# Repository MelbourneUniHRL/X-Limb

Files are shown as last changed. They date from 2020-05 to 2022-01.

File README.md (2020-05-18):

# X-Limb: A Practical 3D-Printed Soft Robotic Prosthetic Hand

Currently, the gap between the existing soft robotic hand designs and the practical requirements significantly hampers the potential to transfer 
these designs to real-world applications. These requirements are:
- Light weight (less than the average weight of a human hand) 
- Intrinsic actuation system (embedded in the hand structure) 
- Robust finger kinematic design and compliance in the mechanical design 
- Powered thumb for multiple grasping types 
- Ease of manufacture and personalisation 
- Sufficient functionalities and the balance between the functionalities and complexity 

The X-Limb hand prosthesis design addressed these requirements with the consideration of the trade-off between practicality and performance.

**More details in the following open-access paper in PLoS ONE:**

[ Mohammadi A, Lavranos J, Zhou H, Mutlu R, Alici G, Tan Y, et al. (2020) A practical 3D-printed soft robotic prosthetic hand with multi-articulating capabilities. PLoS ONE 15(5): e0232766. https://doi.org/10.1371/journal.pone.0232766](https://journals.plos.org/plosone/article?id=10.1371/journal.pone.0232766).

**Performance of the X-Limb in carrying out activities of daily living is available in the following video in YouTube:**

[X-Limb - A Lightweight Soft Robotic Prosthetic Hand](https://youtu.be/qoeMaFlB5xs)

## Main characteristics of the X-Limb design:
**- Overall weight:** 253gr

**- Grasp types:** Three grasps types (power, pinch, and tripod) with capability of individual finger movement

**- Grip force:** Power grasp force of 21.5N and pinch grasp force of 10.2N

**- Hand closing/opening speed:** 1.3sec

**- Cost:** Bill of material cost of 200 USD (excluding quick disconnect wrist but without factoring in the cost reduction through mass production).

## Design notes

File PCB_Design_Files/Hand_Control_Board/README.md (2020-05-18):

## Hand main control board PCB design files

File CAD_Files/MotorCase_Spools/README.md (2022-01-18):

# DC motor cases and spools of different fingers
All these CAD files should be 3D printed with PLA/ABS with 100% infill.

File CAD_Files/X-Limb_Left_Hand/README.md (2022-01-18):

## STL files of the X-Limb left hand
This CAD files should be 3D printed with TPU or TPE flexible filaments. The fingers should be 3D printed in upright position without any support materials.

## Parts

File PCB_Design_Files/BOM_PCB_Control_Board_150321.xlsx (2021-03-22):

# | Designator | Description* | Footprint* | Manufacturer* | Manufacturer Part Number | Supplier | Quantity* | Accept substitution
1 | C1, C2 | 1uf 6.3V | C0603 |  | 0603F105M250NT |  | 2
2 | C5, C7, C8, C9, C10, C11, C12, C13, C14, C15, C16, C17, C18, C19, C20, C27, C28, C29 | 100nF 50V | C0603 |  | 0603F104M500NT |  | 18
3 | CP1, CP2, CP3, CP4, CP5, CP6, CP7 | 47uF 10V | CAPPM5042X550N |  | HV470M010C055R |  | 7
4 | C21, C22, C23, C30, C31, C32 | 33nF 50V | C0603 |  | GRM188R71H333KA61D |  | 6
5 | C24, C25, C26, C33, C34, C35 | 0.47uF 16V | C0603 |  | CL10B474KA8NNNC |  | 6
6 | C4, C6 | 10uF 6.3V | C0603 |  | 0603X106M6R3NT |  | 2
7 | R3, R4, R5, R6, R7, R8, R9, R10, R11, R12, R13, R16, R17, R18, R19, R20, R27, R28, R29, R39, R40, R41, R51, R52 | 1k | 0603 |  | RC0603JR-071KL |  | 26
8 | R2, R14, R15, R21, R22, R23, R24, R25, R26, R33, R34, R35, R36, R37, R38 | 100K | 0603 |  | RC0603JR-07100KL |  | 4
9 | R30, R31, R32, R42, R43, R44 | 220 | 0603 |  | RC0603JR-07220RL |  | 2
10 | R1, R45, R46, R47, R48, R49, R50 | 10k | 0603 |  | RC0603JR-0710KL |  | 7
11 | LED1, LED2, LED3 | LED RED | 0805 |  | 17-21SURC/S530-A3/TR8 |  | 1
12 | D1, D2 | B5819W-TP | SOD-123 | Micro Commercial Co | B5819W-TP (https://www.digikey.cn/en/products/detail/micro-commercial-co/B5819W-TP/3774959?WT.z_header=search_go&s=N4IgTCBcDaIEIFYAcBGAnAdQLQBUAKIAugL5A) | DigiKey | 2
13 | Q2, Q3, Q4, Q5, Q6, Q7 | 2N7002K-T1-GE3 (https://search.ickey.cn/site/index.html?keyword=2N7002K-T1-GE3) | TO-236 | Vishay Siliconix | 2N7002K-T1-GE3 (https://www.digikey.cn/en/products/detail/vishay-siliconix/2N7002K-T1-GE3/2621521?WT.z_header=search_go&s=N4IgTCBcDa4HIHYAMSwGkC0AVAjBg4gKIDMIAugL5A) | DigiKey | 6
14 | Q1 | IRF7842 | 8-SO | Infineon Technologies | IRF7842PBF-ND (https://www.digikey.cn/en/products/detail/infineon-technologies/IRF7842PBF/856673?WT.z_header=search_go&s=N4IgTCBcDaIJICUBiB2AHAFjABQEJIFoA5AERAF0BfIA) | DigiKey | 1
15 | U7, U9, U10, U16, U17, U18 | MC33926 | 32PQFN | NXP USA Inc. | MC33926PNB-ND (https://www.digikey.cn/en/products/detail/nxp-usa-inc/MC33926PNB/2185655?WT.z_header=search_go&s=N4IgTCBcDaILIGEDMSCcYBsAFAcgIQFocAREAXQF8g) | DigiKey | 6
16 | U4, U5, U6, U8, U11, U12 | SN74LVC2G08DCUT (https://search.ickey.cn/site/index.html?keyword=SN74LVC2G08DCUT) | 8VSSOP | Texas Instruments | SN74LVC2G08DCUT (https://www.digikey.cn/en/products/detail/texas-instruments/SN74LVC2G08DCUT/1592265) | DigiKey | 6
17 | U2 | ATmega2560-16AU | 100-TQFP | Microchip Technology | ATMEGA2560-16AU-ND (https://www.digikey.cn/en/products/detail/microchip-technology/ATMEGA2560-16AU/735455?WT.z_header=search_go) | DigiKey | 1
18 | U1 | NCP1117ST50T3G | SOT-223 | ON Semiconductor | NCP1117ST50T3GOSCT-ND (https://www.digikey.cn/en/products/detail/on-semiconductor/NCP1117ST50T3G/921289?WT.z_header=search_go) | DigiKey | 1
19 | Y1 | CSTCE16M0V53-R0 | 3-SMD | Murata Electronics | 490-1198-1-ND (https://www.digikey.cn/en/products/detail/murata-electronics/CSTCE16M0V53-R0/584406?WT.z_header=search_go&s=N4IgTCBcDaICwE4AMBaAjGhAOdKByAIiALoC%2BQA) | DigiKey | 1
20 | U3 | FT232RL | 28-SSOP | FTDI | 895-FT232RL (https://www.digikey.cn/en/products/detail/ftdi-future-technology-devices-international-ltd/FT232RL-REEL/1836385?WT.z_header=search_go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) | DigiKey | 1
21 | RESET | SW-PB |  | TE Connectivity | 450-1129-ND (https://www.digikey.cn/en/products/detail/te-connectivity-alcoswitch-switches/FSM4JSMA/525821?WT.z_header=search_go&s=N4IgTCBcDaICwFYAMBaAjGsBOFA5AIiALoC%2BQA) | DigiKey | 1
22 | M1, M2, M3, M4, M5, M6 | SFW5R-1STE1LF |  | Amphenol ICC (FCI) | 609-1784-1-ND (https://www.digikey.cn/en/products/detail/amphenol-icc-fci/HFW5R-1STE1LF/1002099?WT.z_header=search_go&s=N4IgTCBcDaIGwAYCcBaAjAdgBwBZ0oDkAREAXQF8g) | DigiKey | 6
23 | JC1 | MICRO USB Connector |  | Amphenol ICC (FCI) | 10118192-0001LF (https://www.digikey.cn/en/products/detail/amphenol-icc-fci/10118192-0001LF/2785387?WT.z_header=search_go&s=N4IgTCBcDaIIwAY5wBxwJxgLQN3AMgGIgC6AvkA) | DigiKey | 1

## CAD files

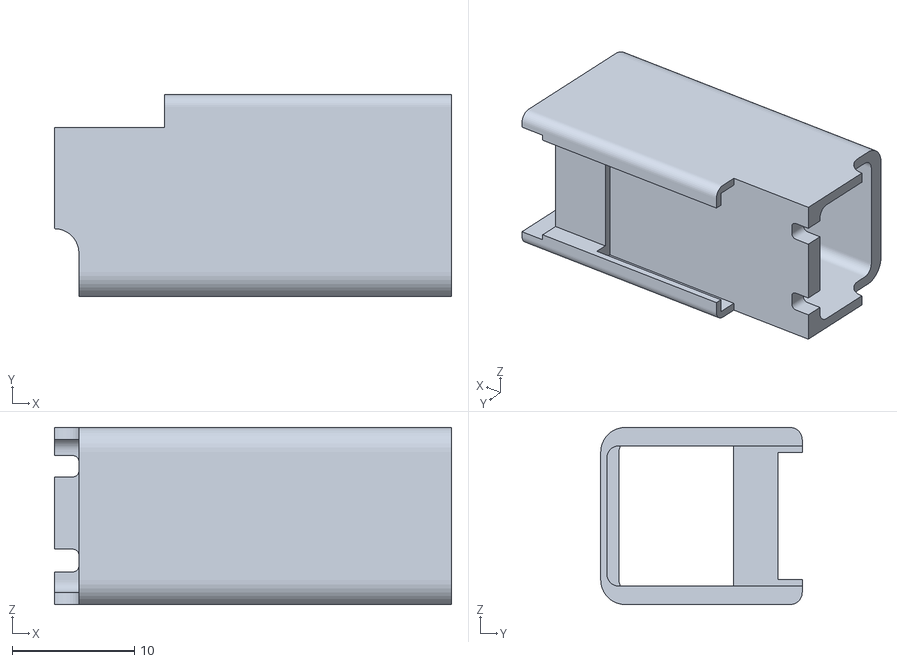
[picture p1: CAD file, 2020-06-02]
CAD_Files/MotorCase_Spools/MotorCaseBody_1000_GearRatio_Index_Middle_Thumb_Ring.STL
32.5 x 16.5 x 14.5

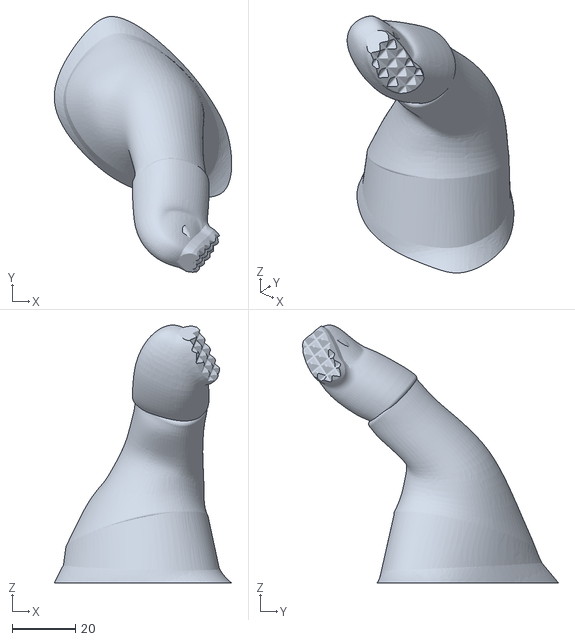
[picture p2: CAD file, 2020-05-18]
CAD_Files/X-Limb_Left_Hand/Left_Hand_Thumb.STL
56.2 x 81.0 x 81.6

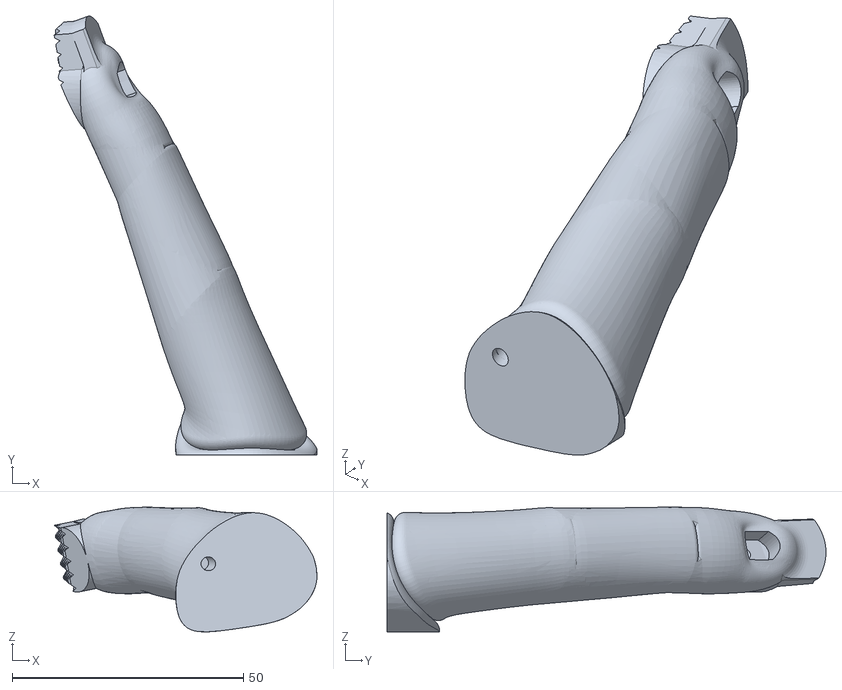
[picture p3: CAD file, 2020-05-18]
CAD_Files/X-Limb_Right_Hand/Right_Hand_Index.STL
56.9 x 94.9 x 27.0

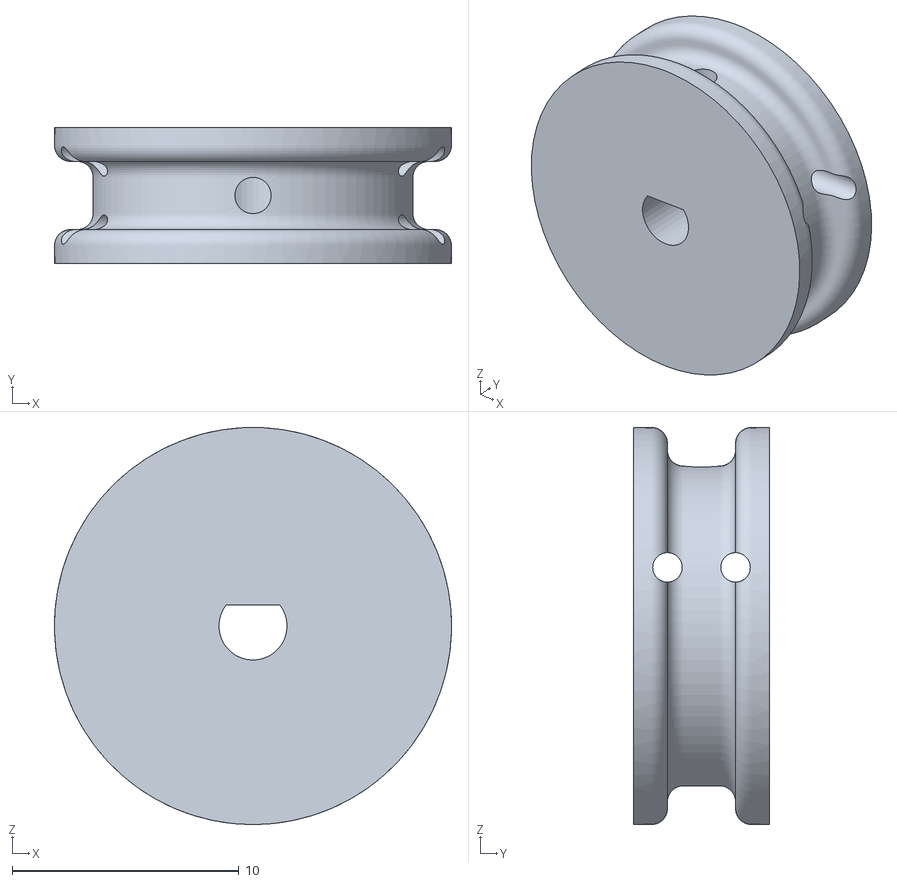
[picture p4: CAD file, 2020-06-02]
CAD_Files/MotorCase_Spools/Spool_17mm_Middle_Ring.STL
17.5 x 6.00 x 17.5

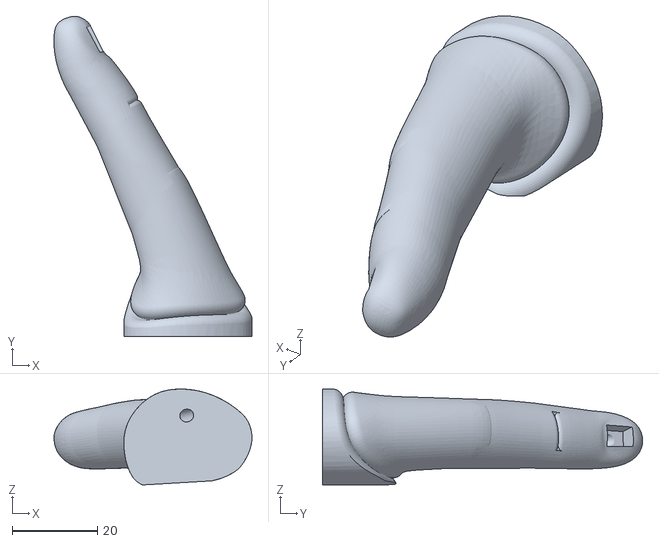
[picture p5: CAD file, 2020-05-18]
CAD_Files/X-Limb_Left_Hand/Left_Hand_Little.STL
46.4 x 75.1 x 22.5

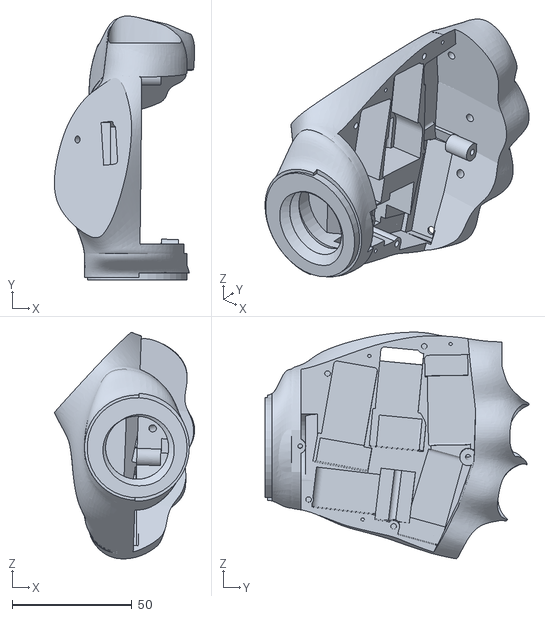
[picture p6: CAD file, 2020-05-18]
CAD_Files/X-Limb_Right_Hand/Righ_Hand_Palm.STL
58.6 x 110.3 x 94.7

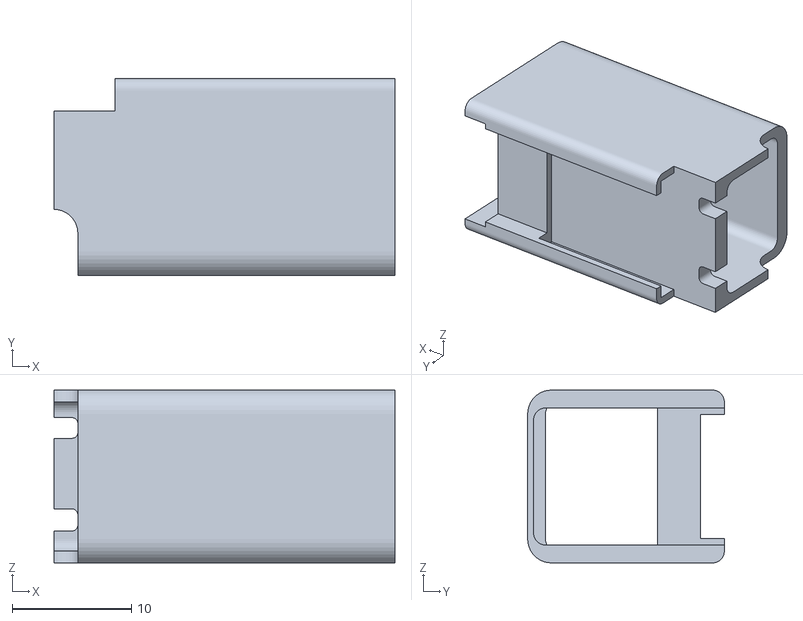
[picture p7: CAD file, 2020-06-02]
CAD_Files/MotorCase_Spools/MotorCaseBody_298_GearRatio_Little.STL
28.6 x 16.5 x 14.5

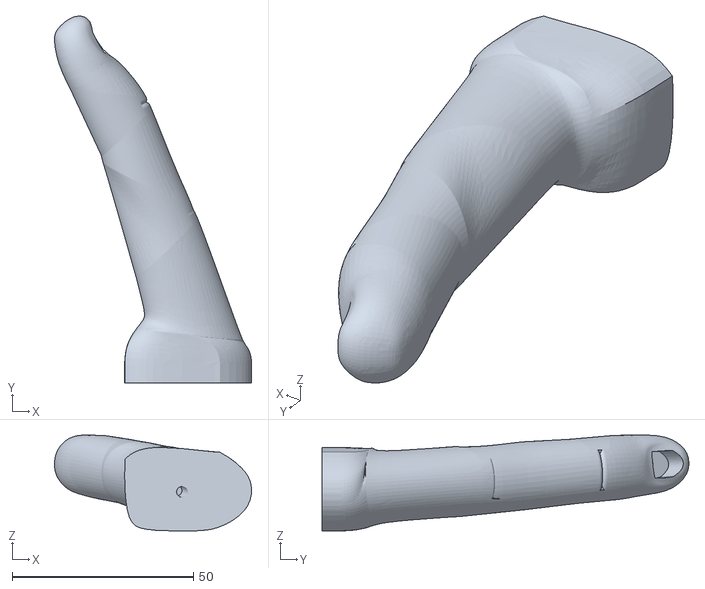
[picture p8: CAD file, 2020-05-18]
CAD_Files/X-Limb_Left_Hand/Left_Hand_Middle.STL
54.4 x 101.2 x 26.4

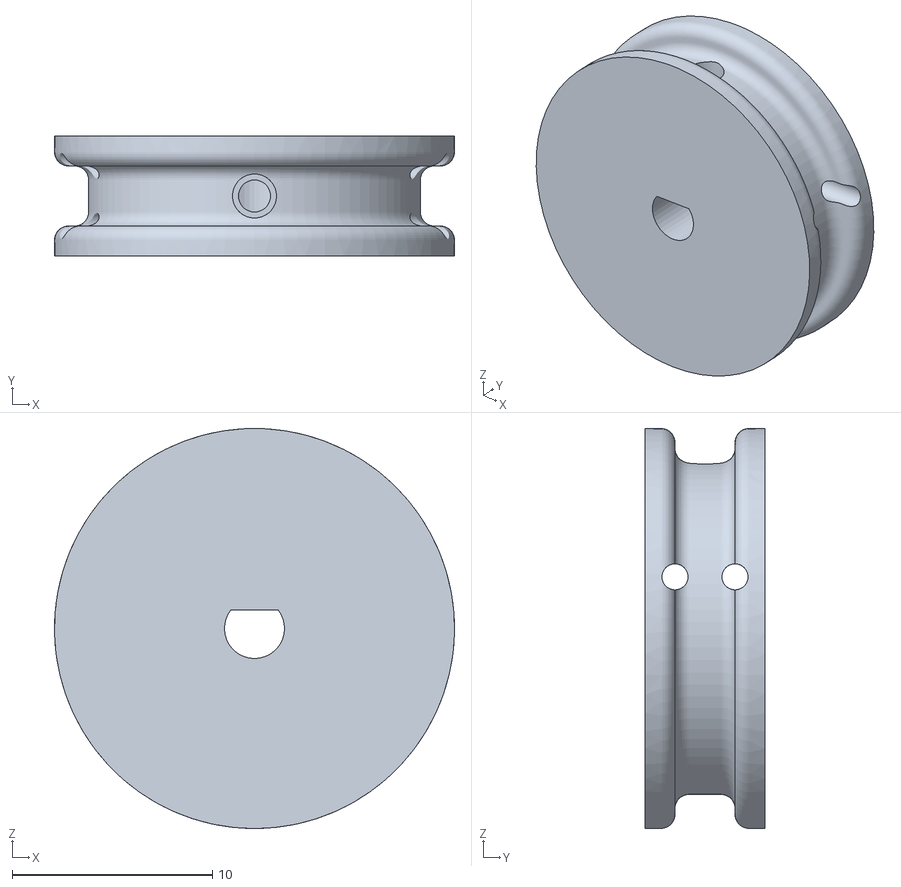
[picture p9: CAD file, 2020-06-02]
CAD_Files/MotorCase_Spools/Spool_20mm_Index_Little_Thumb.STL
20.0 x 6.00 x 20.0

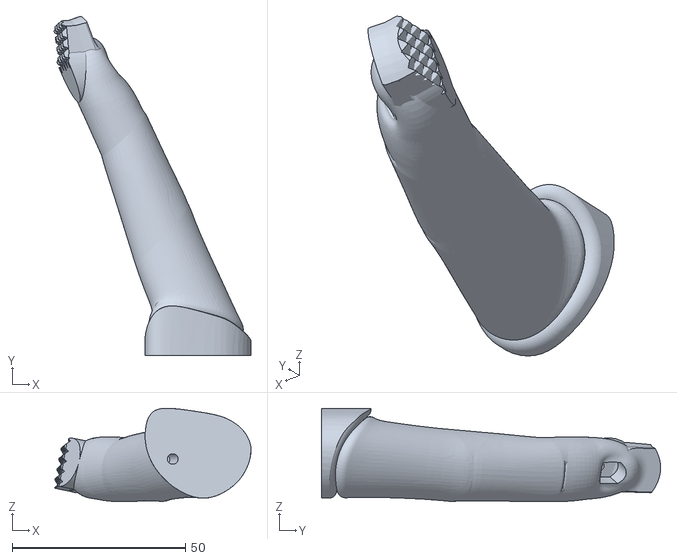
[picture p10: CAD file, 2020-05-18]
CAD_Files/X-Limb_Left_Hand/Left_Hand_Index.STL
56.9 x 97.9 x 27.0

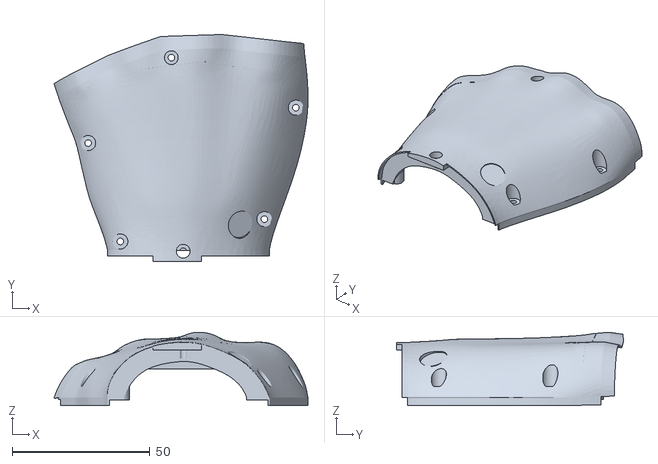
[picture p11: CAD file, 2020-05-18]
CAD_Files/X-Limb_Left_Hand/Left_Hand_Back_Cover.STL
92.1 x 82.3 x 26.6

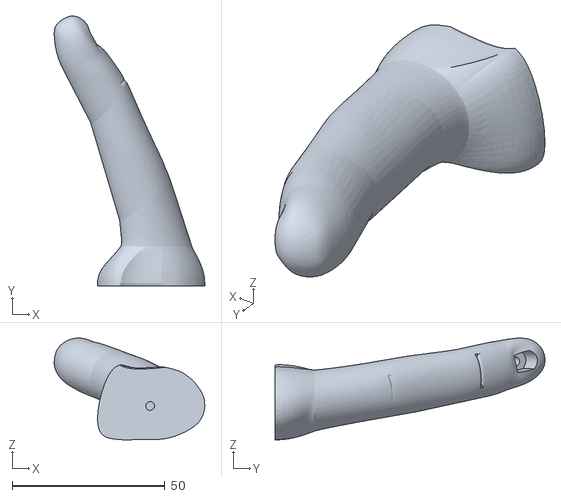
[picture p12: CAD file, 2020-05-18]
CAD_Files/X-Limb_Right_Hand/Right_Hand_Ring.STL
49.3 x 88.4 x 33.4

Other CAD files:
CAD_Files/X-Limb_Right_Hand/Right_Hand_Little.STL
CAD_Files/X-Limb_Right_Hand/Right_Hand_Thumb.STL
CAD_Files/X-Limb_Left_Hand/Left_Hand_Palm.STL
CAD_Files/X-Limb_Right_Hand/Right_Hand_Middle.STL
CAD_Files/X-Limb_Left_Hand/Left_Hand_Ring.STL
CAD_Files/X-Limb_Right_Hand/Right_Hand_Back_Cover.STL

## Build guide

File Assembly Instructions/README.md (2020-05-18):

### Instructive videos for assembly of the X-Limb components

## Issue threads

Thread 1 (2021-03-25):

### ISSUE TITLE
maybe not an issue

### ISSUE THREAD

**Issue by gasparapsag** [MelbourneUniHRL/X-Limb#1]
Hi, 

It's amazing the job that you guys have done with this, I could not find anything similar to this, just amazing! 

I'm trying to build this hand for a cousin who needs it, the thing is when I sent the boom to de PCB manufacturer they said is incomplete as they need the code of the part from mouser or Digikey. I don't know how to correctly choose some of the components as for example for capacitors besides capacitance and footprint voltage is needed to select one and resistor sometimes I can't find the correct footprint.
Here is what I have found so far.
https://drive.google.com/file/d/1TM07XncSh36at8BIBJNJwm0H0ubI7nqd/view?usp=sharing

Could you guys guide me on how to select the rest of the components?

Thank you!

**Comment by MelbourneUniHRL** [comment]
Hi,

We are glad that you found it useful. The PCBs are actually fabricated by contract manufacturer. I can ask them regarding the missing components, probably it will take a bit of time.

If you just need to make one, I have a spare controller which I can post to you at no cost.

Regards,
Alireza


------------------------------------------------------

Alireza Mohammadi
Senior Research Officer,
Department of Mechanical Engineering
The University of Melbourne, Parkville VIC 3010
Phone: +61 3 8345 4378
Email: alirezam@unimelb.edu.au
Webpage: <http://people.eng.unimelb.edu.au/doetomo/> http://people.eng.unimelb.edu.au/alirezam/

________________________________

**Comment by gasparapsag** [comment]
Hi Alireza, 

Such a great news, yes it would be nice if you can post me the controller I will pay the shipping.

Right now I want to make  just one for my cousin, she is a single mother of 4 living in precarious conditions, a few weeks ago she almost took her own life. I wasn’t aware of the psychological problems that amputees have until I got close to one. 
Now you have inspired me to help others too so I will appreciate the full list of components whenever is complete.

Thank you.
Gaspar.

**Comment by MelbourneUniHRL** [comment]
Hi Gaspar,

It is sad to hear that. Just send me your address so I can post it to you.

Her amputation is on her right hand or left hand? Is it below elbow?

I have some other spare parts that can them to you along with the controller.

Regards,
Alireza


------------------------------------------------------

Alireza Mohammadi
Senior Research Officer,
Department of Mechanical Engineering
The University of Melbourne, Parkville VIC 3010
Phone: +61 3 8345 4378
Email: alirezam@unimelb.edu.au
Webpage: <http://people.eng.unimelb.edu.au/doetomo/> http://people.eng.unimelb.edu.au/alirezam/

________________________________

**Comment by gasparapsag** [comment]
Hi Alireza, 

The amputation it’s on her left hand below elbow.
I will send you my address to your email, do you want me to attach a photo of the arm?

Thanks.
Gaspar.

**Comment by MelbourneUniHRL** [comment]
No need for the photo.

Regards,
Alireza


------------------------------------------------------

Alireza Mohammadi
Senior Research Officer,
Department of Mechanical Engineering
The University of Melbourne, Parkville VIC 3010
Phone: +61 3 8345 4378
Email: alirezam@unimelb.edu.au
Webpage: <http://people.eng.unimelb.edu.au/doetomo/> http://people.eng.unimelb.edu.au/alirezam/

________________________________

**Comment by gasparapsag** [comment]
> No need for the photo. Regards, Alireza
> […](#)

Hi Alireza, 

I’ve sent you an email to alirezam@unimelb.edu.au on Tuesday with my personal info, please let me know if you have received it.

Thank you.
Gaspar Catalán.

**Comment by MelbourneUniHRL** [comment]
Yes, I've got you message. I'll send the stuff ASAP.

Regards,
Alireza
________________________________

**Comment by gasparapsag** [comment]
Nice, no worries, just checking in to make sure you received the email.

Thanks.
Gaspar Catalán.

**Comment by MelbourneUniHRL** [comment]
Thanks for your interest. The list has been updated with the link to the parts available in Digikey. The rest of components have been sourced from another company but they are also available in Digikey.

**Comment by gasparapsag** [comment]
Thank you!

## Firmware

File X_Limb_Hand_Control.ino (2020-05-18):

/* This code is developed for control of six DC motors using the custom designed PCB (Arduino Mega compatible)  */
/* In the designed X-Limb hand only 5 motors are used for individual actuation of five fingers of the hand. */



#define STATUS_LED  53


//motors
#define ENABLE  38 // enable/disbale all motors

#define MOTOR_A 1
#define MOTOR_B 2
#define MOTOR_C 3
#define MOTOR_D 4
#define MOTOR_E 5
#define MOTOR_F 6

// Motor A Control
#define POTA    A3 // Potentiometer A
#define FBA     A0  // Current feedback for the motor A 
#define PWMA    7   // Speed control A
#define D2A     11  // enbale(HIGH)/disbale(LOW) for motor A
#define DIRA    12  // Directions for motor A
// Motor B Control
#define POTB    A2 // Potentiometer B
#define FBB     A1  // Current feedback for the motor B 
#define PWMB    4   // Speed control B
#define D2B     8   // enbale(HIGH)/disbale(LOW) for motor B
#define DIRB    9   // Directions for motor B
// Motor C Control
#define POTC    A7 // Potentiometer C
#define FBC     A13 // Current feedback for the motor C 
#define PWMC    5   // Speed control C
#define D2C     39  // enbale(HIGH)/disbale(LOW) for motor C
#define DIRC    29  // Directions for motor C
// Motor D Control
#define POTD    A8 // Potentiometer D
#define FBD     A14 // Current feedback for the motor D 
#define PWMD    2   // Speed control D
#define D2D     25  // enbale(HIGH)/disbale(LOW) for motor D
#define DIRD    26  // Directions for motor D
// Motor E Control
#define POTE    A10 // Potentiometer E
#define FBE     A12 // Current feedback for the motor E
#define PWME    3   // Speed control E
#define D2E     37  // enbale(HIGH)/disbale(LOW) for motor E
#define DIRE    36  // Directions for motor E
// Motor F Control
#define POTF    A9 // Potentiometer F
#define FBF     A11 // Current feedback for the motor F
#define PWMF    6   // Speed control F
#define D2F     19  // enbale(HIGH)/disbale(LOW) for motor F
#define DIRF    18  // Directions for motor F

void setup() {
  // put your setup code here, to run once:
  
  Serial.begin(115200);

  pinMode(STATUS_LED, OUTPUT);
  
  pinMode(ENABLE, OUTPUT);
  digitalWrite(ENABLE, LOW);    // Disable all motors
  
  pinMode(D2C, OUTPUT);
  pinMode(DIRC, OUTPUT);
  pinMode(FBC, INPUT);
  pinMode(PWMC, OUTPUT);  //  setPwmFrequency2560(PWMC, 1);
  
  // Enables
  pinMode(D2A, OUTPUT);
  pinMode(D2B, OUTPUT);
  pinMode(D2C, OUTPUT);
  pinMode(D2D, OUTPUT);
  pinMode(D2E, OUTPUT);
  pinMode(D2F, OUTPUT);

 // Enables value
  digitalWrite(D2A, HIGH);
  digitalWrite(D2B, HIGH);
  digitalWrite(D2C, HIGH);
  digitalWrite(D2D, HIGH);
  digitalWrite(D2E, HIGH);
  digitalWrite(D2F, HIGH);

  // Directions
  pinMode(DIRA, OUTPUT);
  pinMode(DIRB, OUTPUT);
  pinMode(DIRC, OUTPUT);
  pinMode(DIRD, OUTPUT);
  pinMode(DIRE, OUTPUT);
  pinMode(DIRF, OUTPUT);

  // Directions value
  digitalWrite(DIRA, HIGH);  
  digitalWrite(DIRB, LOW);  
  digitalWrite(DIRC, LOW);  
  digitalWrite(DIRD, HIGH);  
  digitalWrite(DIRE, HIGH);  
  digitalWrite(DIRF, LOW);  

  // PWM
  pinMode(PWMA, OUTPUT);  //  setPwmFrequency2560(PWMC, 1);
  pinMode(PWMB, OUTPUT);  //  setPwmFrequency2560(PWMC, 1);
  pinMode(PWMC, OUTPUT);  //  setPwmFrequency2560(PWMC, 1);
  pinMode(PWMD, OUTPUT);  //  setPwmFrequency2560(PWMC, 1);
  pinMode(PWME, OUTPUT);  //  setPwmFrequency2560(PWMC, 1);
  pinMode(PWMF, OUTPUT);  //  setPwmFrequency2560(PWMC, 1);

  // PWM value
  analogWrite(PWMA, 0);
  analogWrite(PWMB, 0);
  analogWrite(PWMC, 0);
  analogWrite(PWMD, 0);
  analogWrite(PWME, 0);
  analogWrite(PWMF, 0);

  // Current feedback
  pinMode(FBA, INPUT);
  pinMode(FBB, INPUT);
  pinMode(FBC, INPUT);
  pinMode(FBD, INPUT);
  pinMode(FBE, INPUT);
  pinMode(FBF, INPUT);

  // Position feedback
  pinMode(POTA, INPUT);
  pinMode(POTB, INPUT);
  pinMode(POTC, INPUT);
  pinMode(POTD, INPUT);
  pinMode(POTE, INPUT);
  pinMode(POTF, INPUT);

  digitalWrite(ENABLE, HIGH); 
 
}

unsigned int CommandCloseOpen; // Closing/Opening the hand
unsigned int CommandGraspType;  // Switching to the desired grip

// Variables for potentiometer values
unsigned int PotA; 
unsigned int PotB; 
unsigned int PotC; 
unsigned int PotD; 
unsigned int PotE;  
unsigned int PotF;

// Variables for motor current values
unsigned int CurrentA;
unsigned int CurrentB;
unsigned int CurrentC;
unsigned int CurrentD;
unsigned int CurrentE;
unsigned int CurrentF;

// Variables for motors opening and closing speed
unsigned int speedA_Close=90; unsigned int speedA_Open=80; 
unsigned int speedB_Close=100; unsigned int speedB_Open=90; 
unsigned int speedC_Close=50; unsigned int speedC_Open=40;
unsigned int speedD_Close=0; unsigned int speedD_Open=0;
unsigned int speedE_Close=90; unsigned int speedE_Open=80; 
unsigned int speedF_Close=100; unsigned int speedF_Open=90;


// Zero motor speeds
//unsigned int speedA_Close=0; unsigned int speedA_Open=0; 
//unsigned int speedB_Close=100; unsigned int speedB_Open=90; 
//unsigned int speedC_Close=0; unsigned int speedC_Open=0;
//unsigned int speedD_Close=0; unsigned int speedD_Open=0;
//unsigned int speedE_Close=100; unsigned int speedE_Open=90; 
//unsigned int speedF_Close=0; unsigned int speedF_Open=0;

// Grasp type
unsigned int Type=1;
  
void loop() {



// Reading potentimeter values
   PotA = analogRead(A3);  Serial.print("  PotA: "); Serial.println(PotA);
   PotB = analogRead(A2);  Serial.print("  PotB: "); Serial.println(PotB);
   PotC = analogRead(A7);  Serial.print("  PotC: "); Serial.println(PotC);
 //  PotD = analogRead(A8);  Serial.print("  PotD: "); Serial.println(PotD);
   PotE = analogRead(A10);  Serial.print("  PotE: "); Serial.println(PotE);
   PotF = analogRead(A11);  Serial.print("PotF: "); Serial.println(PotF);

// Reading current values
//  CurrentA=analogRead(A0);  Serial.print("CurrentA: "); Serial.println(CurrentA);
//  CurrentB=analogRead(A1);  Serial.print("CurrentB: "); Serial.println(CurrentB);
//  CurrentC=analogRead(A13);  Serial.print("CurrentC: "); Serial.println(CurrentC);
//  CurrentD=analogRead(A14);  Serial.print("CurrentD: "); Serial.println(CurrentD);
//  CurrentE=analogRead(A12);  Serial.print("CurrentE: "); Serial.println(CurrentE);
//  CurrentF=analogRead(A11);  Serial.print("CurrentF: "); Serial.println(CurrentF);


  CommandCloseOpen = analogRead(A4);   
  CommandGraspType = analogRead(A5);   
   


   Serial.print("CommandCloseOpen: "); Serial.print(CommandCloseOpen);
   Serial.print("   CommandGraspType: "); Serial.print(CommandGraspType);


 if (CommandGraspType<100){ 
  delay(600);
    Type=Type+1;
    if (Type>3){
        Type=3;
    }
 }

  if (CommandGraspType>1000){ 
      delay(600);
    Type=Type-1;
    if (Type<1){
        Type=1;
    }
 }

  Serial.print("   GraspType: "); Serial.print(Type);


//Type=3;
//************* Pinch Grasp ****************//

if (Type==1) {

     PotA = analogRead(A3); PotB = analogRead(A2); PotC = analogRead(A7); PotE = analogRead(A10); PotF = analogRead(A11); 

//            Close Fingers

if (CommandCloseOpen<100){ 

  // Thumb
   if (PotE<750){
     digitalWrite(DIRE, HIGH); 
     analogWrite(PWME, map(speedE_Close, 0, 100, 0, 255));}
   else{
     analogWrite(PWME, map(0, 0, 100, 0, 255));}

// Index
     if (PotA<800){
       if (PotE>650){
       digitalWrite(DIRA, HIGH); 
       analogWrite(PWMA, map(speedA_Close, 0, 100, 0, 255));}}
     else{
       analogWrite(PWMA, map(0, 0, 100, 0, 255));}

      
     
     }
else if(CommandCloseOpen>1000){

    // Thumb
   if (PotE>250){
     if (POTA<200){
     digitalWrite(DIRE, LOW); 
     analogWrite(PWME, map(speedE_Open, 0, 100, 0, 255));}}
   else{
     analogWrite(PWME, map(0, 0, 100, 0, 255));}

// Index
     if (PotA>100){
       digitalWrite(DIRA, LOW); 
       analogWrite(PWMA, map(speedA_Open, 0, 100, 0, 255));}
     else{
       analogWrite(PWMA, map(0, 0, 100, 0, 255));}

       
     
     }
     
 else{
     analogWrite(PWMA, map(0, 0, 100, 0, 255));
     analogWrite(PWMB, map(0, 0, 100, 0, 255));
     analogWrite(PWMC, map(0, 0, 100, 0, 255));
     analogWrite(PWMD, map(0, 0, 100, 0, 255));
     analogWrite(PWME, map(0, 0, 100, 0, 255));
     analogWrite(PWMF, map(0, 0, 100, 0, 255));}

}



//************* Tripod Grasp ****************//

if (Type==2) {

     PotA = analogRead(A3); PotB = analogRead(A2); PotC = analogRead(A7); PotE = analogRead(A10); PotF = analogRead(A11); 

//            Close Fingers

if (CommandCloseOpen<100){ 

// Thumb
   if (PotE<800){
     digitalWrite(DIRE, HIGH); 
     analogWrite(PWME, map(speedE_Close, 0, 100, 0, 255));}
   else{
     analogWrite(PWME, map(0, 0, 100, 0, 255));}

// Index
     if (PotA<980){
       if (PotE>600){
       digitalWrite(DIRA, HIGH); 
       analogWrite(PWMA, map(speedA_Close, 0, 100, 0, 255));}}
     else{
       analogWrite(PWMA, map(0, 0, 100, 0, 255));}

// Middle
     if (PotB>500){
       if (PotE>600){
       digitalWrite(DIRB, LOW); 
       analogWrite(PWMB, map(speedB_Close, 0, 100, 0, 255));}}
     else{
       analogWrite(PWMB, map(0, 0, 100, 0, 255));}

       
// Ring
     if (PotF>400){
       digitalWrite(DIRF, LOW); 
       analogWrite(PWMF, map(speedF_Close, 0, 100, 0, 255));}
     else{
       analogWrite(PWMF, map(0, 0, 100, 0, 255));} 
       
// Little
     if (PotC>200){
       digitalWrite(DIRC, LOW); 
       analogWrite(PWMC, map(speedC_Close, 0, 100, 0, 255));}
     else{
       analogWrite(PWMC, map(0, 0, 100, 0, 255));}
     
     }
else if(CommandCloseOpen>1000){

// Thumb
   if (PotE>100){
     if (POTA<200){
     digitalWrite(DIRE, LOW); 
     analogWrite(PWME, map(speedE_Open, 0, 100, 0, 255));}}
   else{
     analogWrite(PWME, map(0, 0, 100, 0, 255));}

// Index
     if (PotA>150){
       digitalWrite(DIRA, LOW); 
       analogWrite(PWMA, map(speedA_Open, 0, 100, 0, 255));}
     else{
       analogWrite(PWMA, map(0, 0, 100, 0, 255));}

// Middle
     if (PotB<960){
       digitalWrite(DIRB, HIGH); 
       analogWrite(PWMB, map(speedB_Open, 0, 100, 0, 255));}
     else{
       analogWrite(PWMB, map(0, 0, 100, 0, 255));}       

// Ring
     if (PotF<980){
           if (POTA<200){
       digitalWrite(DIRF, HIGH); 
       analogWrite(PWMF, map(speedF_Open, 0, 100, 0, 255));}}
     else{
       analogWrite(PWMF, map(0, 0, 100, 0, 255));} 

// Little
     if (PotC<790){
           if (POTA<200){
       digitalWrite(DIRC, HIGH); 
       analogWrite(PWMC, map(speedC_Open, 0, 100, 0, 255));}}
     else{
       analogWrite(PWMC, map(0, 0, 100, 0, 255));} 
            
     }
 else{
     analogWrite(PWMA, map(0, 0, 100, 0, 255));
     analogWrite(PWMB, map(0, 0, 100, 0, 255));
     analogWrite(PWMC, map(0, 0, 100, 0, 255));
     analogWrite(PWMD, map(0, 0, 100, 0, 255));
     analogWrite(PWME, map(0, 0, 100, 0, 255));
     analogWrite(PWMF, map(0, 0, 100, 0, 255));}

}


//************* Power Grasp ****************//

if (Type==3) {

     PotA = analogRead(A3); PotB = analogRead(A2); PotC = analogRead(A7); PotE = analogRead(A10); PotF = analogRead(A11); 

//            Close Fingers

if (CommandCloseOpen<100){ 

  // Thumb
   if (PotE<750){
     digitalWrite(DIRE, HIGH); 
     analogWrite(PWME, map(speedE_Close, 0, 100, 0, 255));}
   else{
     analogWrite(PWME, map(0, 0, 100, 0, 255));}

// Index
     if (PotA<800){
       digitalWrite(DIRA, HIGH); 
       analogWrite(PWMA, map(speedA_Close, 0, 100, 0, 255));}
     else{
       analogWrite(PWMA, map(0, 0, 100, 0, 255));}

// Little
     if (PotC>200){
       digitalWrite(DIRC, LOW); 
       analogWrite(PWMC, map(speedC_Close, 0, 100, 0, 255));}
     else{
       analogWrite(PWMC, map(0, 0, 100, 0, 255));} 
              
// Middle
     if (PotB>100){
       digitalWrite(DIRB, LOW); 
       analogWrite(PWMB, map(speedB_Close, 0, 100, 0, 255));}
     else{
       analogWrite(PWMB, map(0, 0, 100, 0, 255));}

// Ring
     if (PotF>300){
       digitalWrite(DIRF, LOW); 
       analogWrite(PWMF, map(speedF_Close, 0, 100, 0, 255));}
     else{
       analogWrite(PWMF, map(0, 0, 100, 0, 255));} 
       

     }
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

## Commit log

2020-05-18 Videos of X-Limb assembly
2020-09-02 Position Sensor
2020-09-02 Assembly of heat shrink and potentiometer on motor
2021-03-22 Updated BOM List
    [BOM_PCB_Control_Board_150321.xlsx]
